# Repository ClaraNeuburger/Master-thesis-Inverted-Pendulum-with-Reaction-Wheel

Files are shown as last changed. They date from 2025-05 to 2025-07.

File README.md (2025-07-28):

# Inverted Pendulum Actuated by a Reaction Wheel

This github repository contains the codes (Arduino and Matlab) and CAD files used to create a 2D inverted pendulum actuated by a reaction wheel. 
This project was carried out to support the teaching of control engineering at the SAAS (Service d’Automatique et d’Analyse des Systèmes, https://saas.ulb.ac.be/) laboratory at ULB. The resulting Master thesis text is also available in this repository under *'Master Thesis Text.pdf'*.

## Overview
It consists of a rigid pendulum rod placed on a surface which will be stabilized in the upright position using a motor coupled to a wheel placed on top of the pendulum as shown bellow. 

<p align="center">
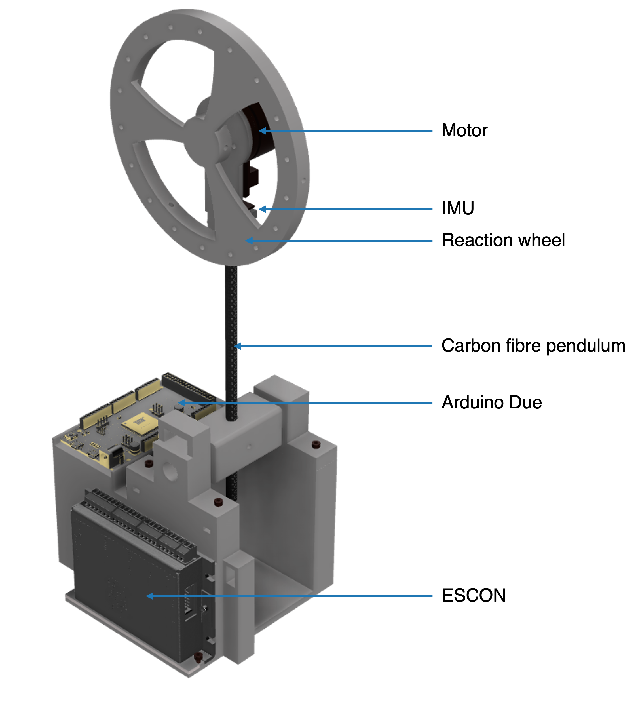
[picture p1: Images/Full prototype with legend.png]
  
</p>

A video of the working prototype is available in the following link: https://www.youtube.com/shorts/VWwU4DCKMfk

The following sections provide a detailed description of the prototype development process. They cover the design and fabrication of 3D-printed components, the selection of the motor and its integration with the driver and the choice and programming of the microcontroller.

## Microcontroller
The Arduino Due was selected as the development board for this project due to its higher computational performance and advanced features. Its 84 MHz clock speed enables faster signal processing, essential for real-time applications. The Due provides a DAC (Digital-to-Analog Converter) for smoother analog outputs, as well as a larger SRAM (96 kB), allowing efficient handling of complex computations and storage of runtime variables.

<p align="center">
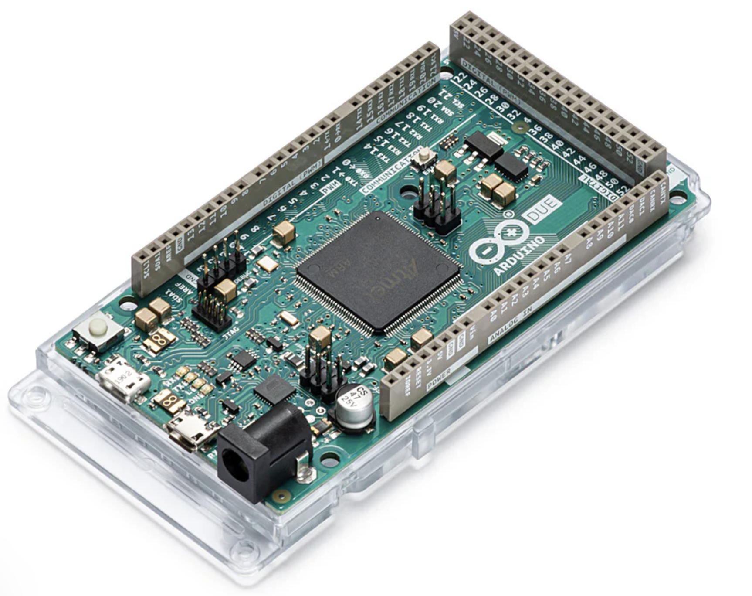
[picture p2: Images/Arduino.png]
  
</p>

The codes implemented on the microcontroller for controlling the pendulum are available in the folder 'Arduino'. 

- Scripts starting with *MPU6050* handle the data received from the Inertial Measurement Unit (IMU) and taken from: https://github.com/jrowberg/i2cdevlib
- File *Variables.ino* defines all variables used for the real time control of the pendulum
- File *main.ino* conatins the live script for controlling the pendulum

## Motor
The motor should be as lightweight as possible while also providing maximum torque. A Maxon brushless DC motor was selected: the EC 45 Flat. 
<p align="center">
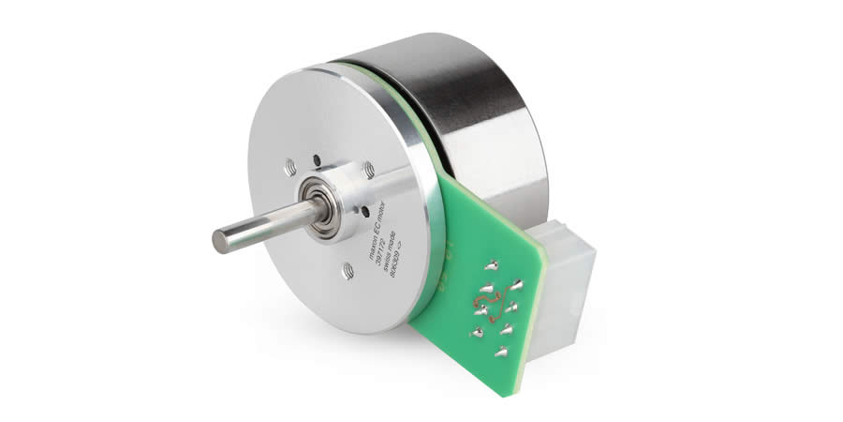
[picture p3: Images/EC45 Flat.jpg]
  
</p>

This type of motor offers an attractive price to performance ratio, a high torques due to external multipole rotor, and a flat and light design meant for limited space. 
The properties of the motor are shown in the table bellow.
<p align="center">
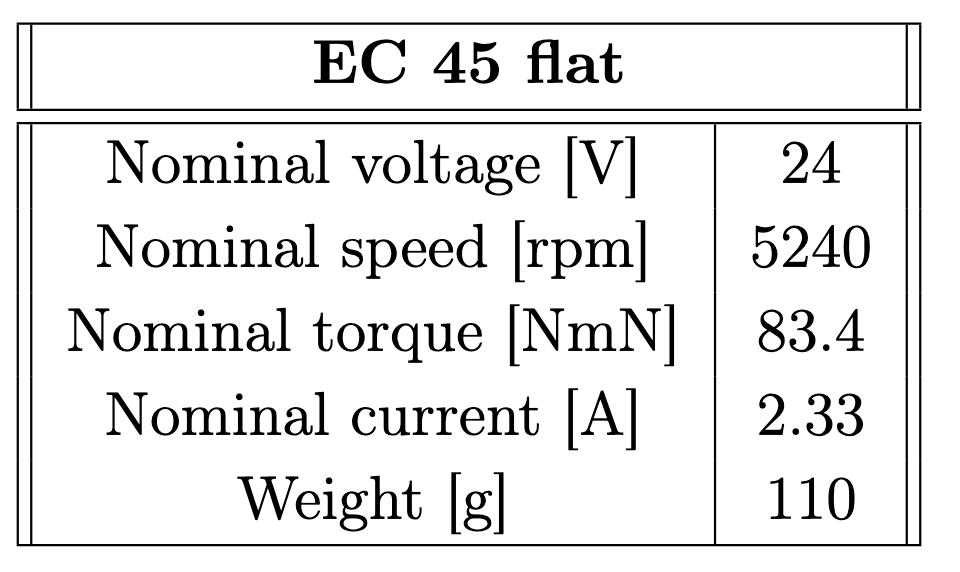
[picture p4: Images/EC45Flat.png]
  
</p>

Link for the motor: https://befr.rs-online.com/web/p/dc-motors/0495063
## Driver
In order to control the motor using the microcontroller, a driver needs to be used. A driver serves as the interface between the motor and the microcontroller to control the motor’s speed, direction or other parameter.

The ESCON 50/5 from Maxon compatible with the motor was chosen. 
<p align="center">
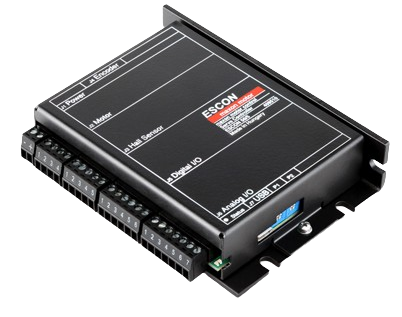
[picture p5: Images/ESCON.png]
  
</p>

It has 3 integrated operating modes: 

 - Current controller which compares the actual motor current with the applied set value and dynamically adjusts it in case of deviation
 - Closed loop speed controller that compares the actual speed with the applied set value and dynamically adjusts it
 - Open loop speed controller that feeds the motor with a voltage proportional to theset value; the load changes are compensated with IxR methodology

The properties of the driver are shown in the table bellow. 
<p align="center">
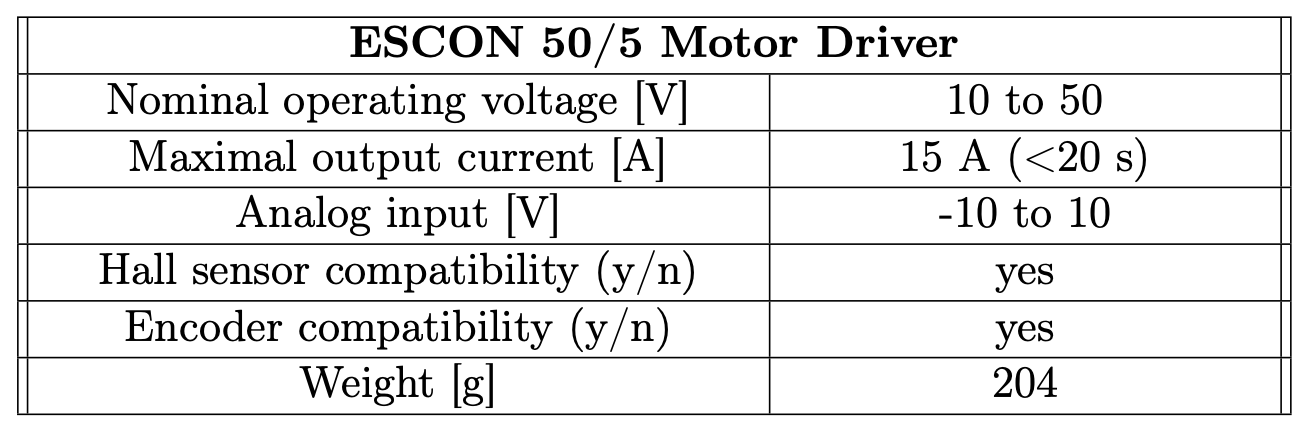
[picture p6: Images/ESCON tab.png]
  
</p>

The ESCON 50/5 is a programmable driver: on a software developed by Maxon, the user can enter the motor's propreties and select one of the 3 operating modes to control the motor. 

The following process was followed when laucnhing the start up wizard tool: 
- **Motor type**: Select maxon EC motor
- **Motor data**: Enter motor speed constant (285 rpm/V), thermal time constant winding (17.7s) and number of pole pairs (8)
- **System data**: Enter desired maximum speed (5240 rpm but you can increase if needed), nominal current (2.33 A) and max output current limit
- **Detection of rotor position**: Select digital Hall sensors with Maxon Hall sensor polarity
- **Speed sensor**: Select available Hall effect sensor
- **Mode of operation**: Select current controller
- **Enable**: Select your desired digital input with high active. In this situation, a switch was placed between digital Input 2 and the +5Vdc of the ESCON to easily enable the motor
- **Set value**: Select analog set value, with the analog input connected to the DAC pin of the microcontroller (here analog input 1). Since the Arduino DAC output is able to send voltages from 0.55 V to 2.75 V, the current sent at 0.55 V is set at -2.33 A and the current sent at 2.75 V is set at 2.33 A.
- ADD SPEED RAMP, OFFSET AND MINIMAL SPEED (need to check the computer for that)
- Add Analog output as well for understanding hall effect sensor outpur

A voltage of at least 22.79 V is required to power the ESCON 50/5 driving the EC45 Flat and a power supply of 24V has been selected. 

Link for the driver: https://www.maxongroup.fr/maxon/view/product/control/4-Q-Servokontroller/409510
## Sensors
### Inertial Measurement Unit (IMU)
To recover the pendulum angle and angular speed an inertial measurement unit can be used. It consists of a combination of accelerometer and gyroscope that allows to measure and report the angular rate of a structure. The accelerometer measures changes of acceleration in the sensor with respect to the earth while the gyroscope measures changing angular motion. The chosen IMU is the MPU6050 linked to an I2C bus for easier connection with the Arduino microcontroller 

<p align="center">
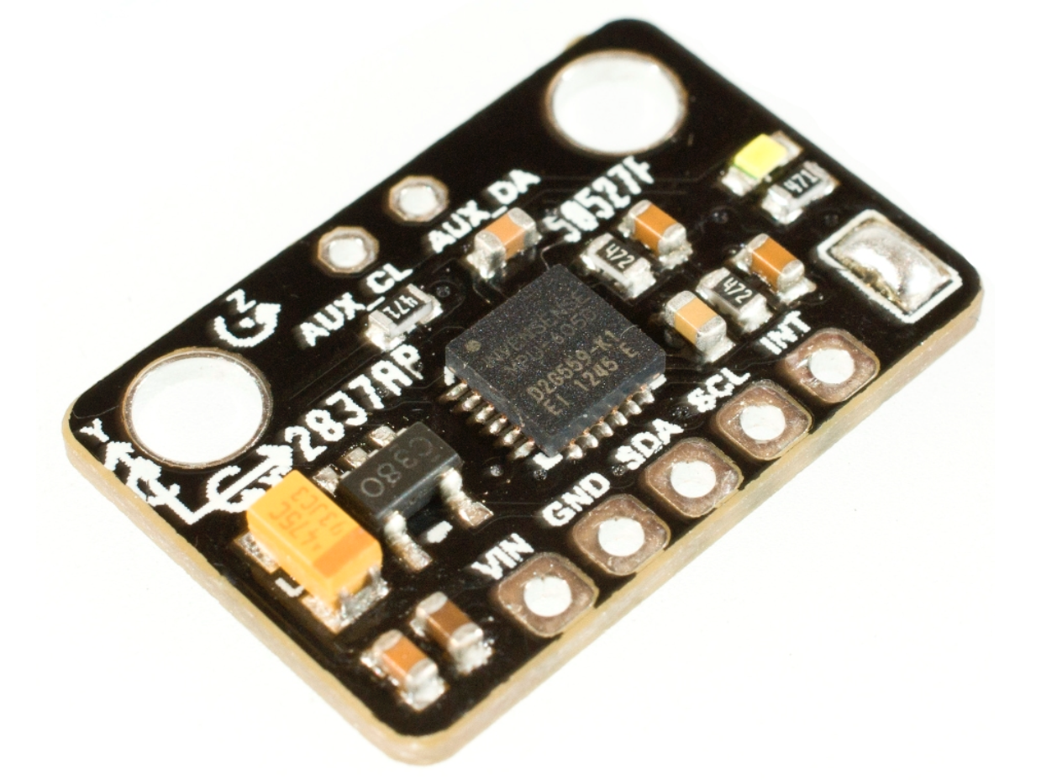
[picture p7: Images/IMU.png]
  
</p>

It has a 3 axis gyroscope and accelerometer, allowing to recover the angle and acceleration in the 3 planes(x,y,z). Using the MPU6050 Arduino library from i2cdevlib, it is
possible to retrieve the Euler angles of the pendulum with the function **mpu.dmpGetEuler()**. By filtering the angle value and doing a derivative, the pendulum angular velocity can also be determined.

Link for the MPU6050: https://be.farnell.com/fr-BE/dfrobot/sen0142/6-dof-sensor-arduino-board/dp/3769961
### Hall effect sensors
To measure the motor’s properties, the EC 45 Flat comes with integrated Hall sensors. Hall sensors detect the magnetic field of a control magnet which is attached to the shaft.
The sensors are arranged between the stator teeth and monitor directly the poles of the magnetic ring with offsets of 120°. The Hall sensors evaluate the direction of the magnetic field and generate a high output (5V) if the north pole of the control magnet is close and a low output (GND) if the south pole is close.

The ESCON 50/5 can automatically recover the motor’s speed and send it via a programmable analog output. The Arduino Due board can recover an analog input range of 0 to 3.3V and the ESCON drier is programmed to send a voltage of 0 V for a speed of -5240 rpm and 3.3 V for a speed ot 5240 rpm.

## Wiring diagram
The wiring diagram of the inverted pendulum with reaction wheel is illustrated bellow.
<p align="center">
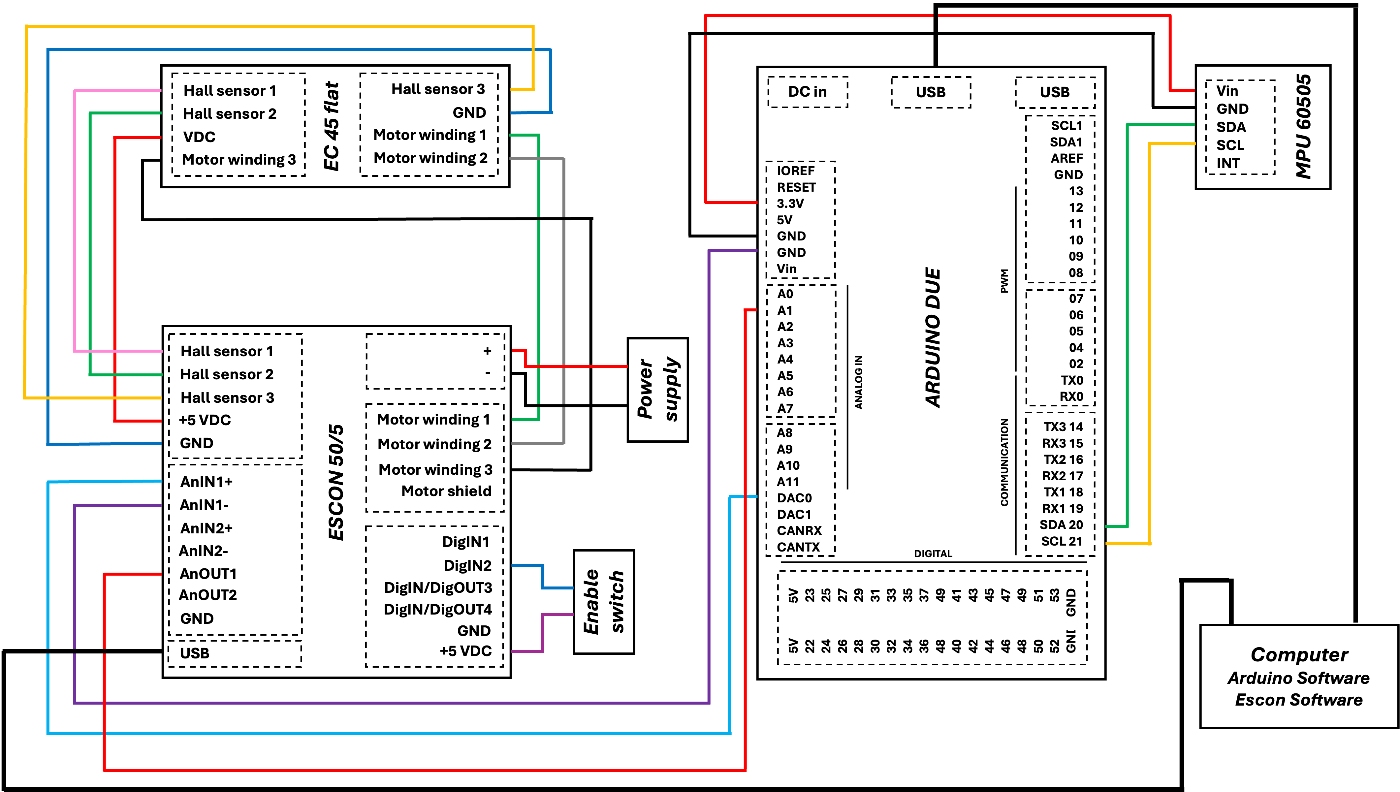
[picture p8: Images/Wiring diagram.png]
  
</p>

## 3D design and printing
The prototype was mainly 3D-printed except for the pendulum rod made of carbon fiber (30cm long hollow cylinder of outer radius 7.5mm). All other components were designed on Fusion360 and 3D-printed in PLA. The CAD files are available in the folder *'Fusion360'*.

A short readme is available in this folder and explains the role of each component and how they are connected to each other. 

The final prototype is shown bellow.
<p align="center">
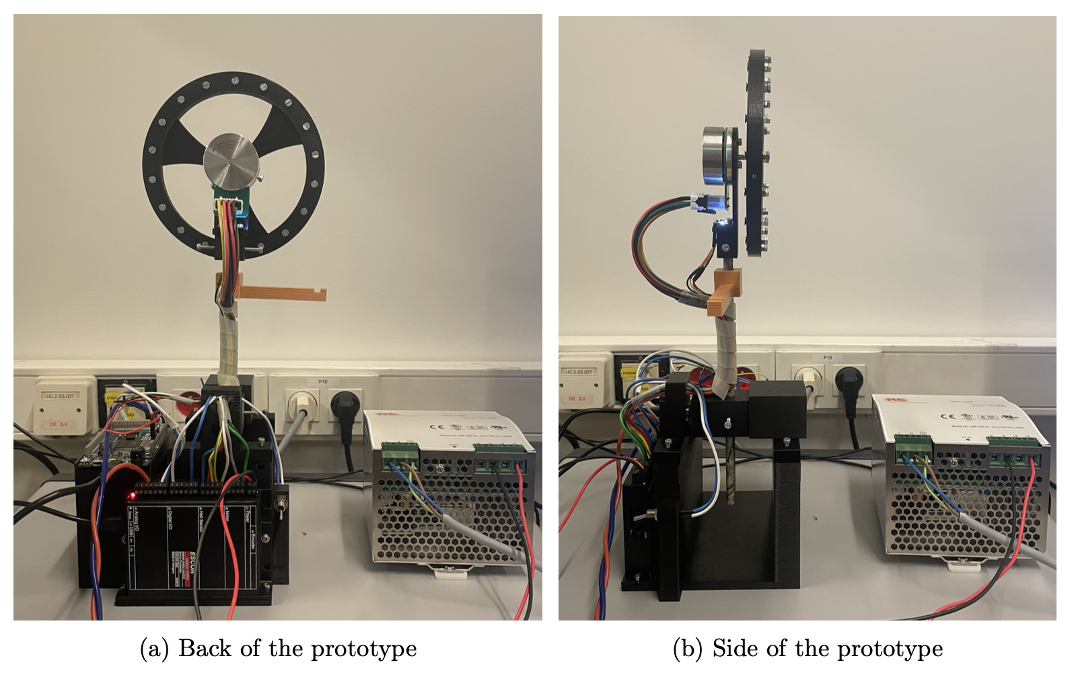
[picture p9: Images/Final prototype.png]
  
</p>

## Matlab code for controlling the pendulum
A series of Matlab code and simulations is available in the folder *Matlab* of this Github. They were developed to establish the control laws to control the pendulum. 

Firstly, a mathematical model of the pendulum was developed and verified experimentally. This is developed in the section *'Mathematical model'* of the Master thesis text.  The code *'model_verif.m'* is used to superpose the experimental results to the simulation results computed by using Simulink file *'Verification_simulink.slx'*. The pendululm was placed upside down, with a current command of 1A during 1 second.

Codes *'Identification_TF.m'*, *'cost_TF.m'* and *'verification.m'* are used to identify and verify the transfer function of the motor (speed response to a current step input).

There are 2 controllers tested: a cascade PID controller and an Linear Quadratic Regulator. The LQR is tuned and the gain is computed using the code *'LQR.m'*, it can then be verified using the simulation *'RegulatorTesting.slx'*.

The cascade PID is tuned using code *'CascadePID.m'* and tested using simulation *'PIDcascadeTuning.slx'*.

Only the LQR worked experimentally, more details are available in the written master thesis.

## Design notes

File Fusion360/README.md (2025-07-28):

This folder contains all the pieces designed on Fusion3D software and 3D printed to create the inverted pendulum with reaction wheel prototype. 

The support structure serves as base to receive the microcontroller (Arduino) and driver (ESCON). They however have some dimensioning issue in terms of the holes to insert screws to secure the 2 parts. 
<p align="center">
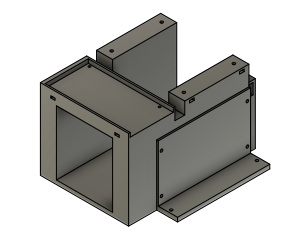
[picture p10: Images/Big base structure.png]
  
</p>

On this support structure are placed 2 'base structure' shown bellow. One is designed with a hole on top to allow the cables to directly reach the top of the driver for connection. 
<p align="center">
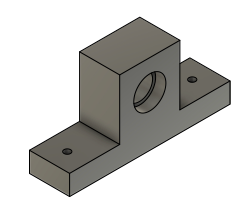
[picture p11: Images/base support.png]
  
</p>

<p align="center">
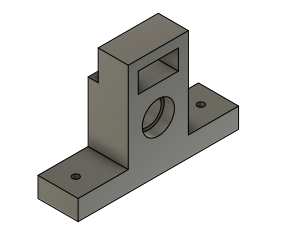
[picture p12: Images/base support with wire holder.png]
  
</p>

Between those 2 bases are places ball bearings (add dimensions) as well as a rectangular holder in which the pendulum is placed and secured with screws. 
<p align="center">
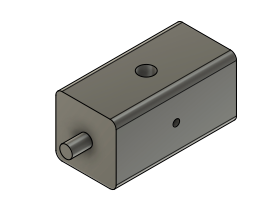
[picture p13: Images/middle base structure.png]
  
</p>

On top of the pendulum is placed the upper structure meant to link with the motor and the inertial measurement unit.
<p align="center">
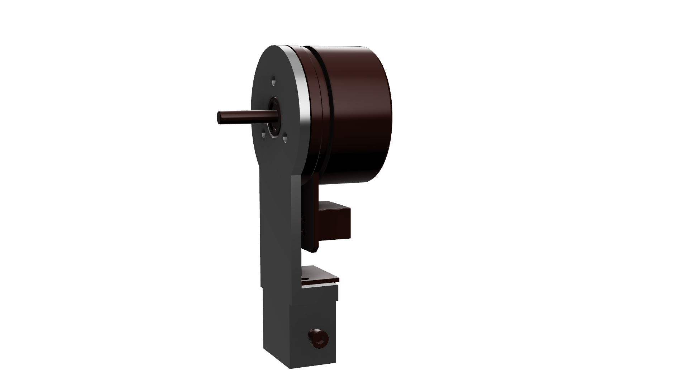
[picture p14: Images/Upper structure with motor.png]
  
</p>

 The reaction wheel is linked to the motor and holes are designed to add screws and nuts to increase its inertia. 
 
<p align="center">
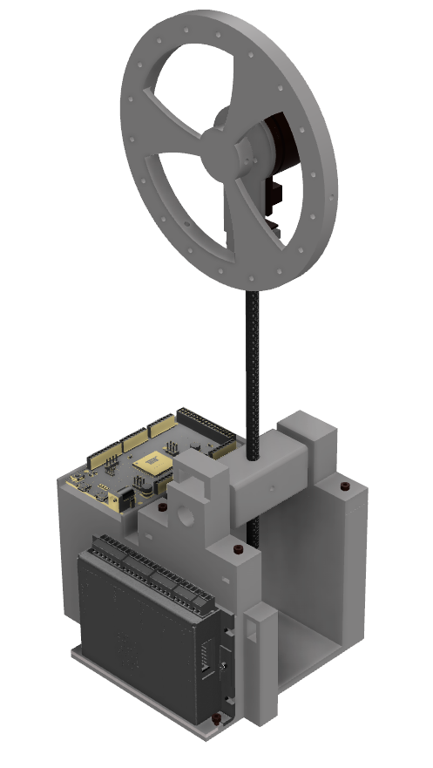
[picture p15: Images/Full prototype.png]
  
</p>

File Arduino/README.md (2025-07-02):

This folder contains all the Arduino scripts used to control the pendulum. 

All the files meant to recover the pendulum's variables from the inertial measurement unit start with 'MPU6050' and where taken from: https://github.com/jrowberg/i2cdevlib

File MPU6050.ino is meant to recover the pendulum angle during live script. 

File Variables.ino defines all variables used in the main file. 

The main.ino file contains the live script to control the Arduino. It recovers the pendulum angle, angular speed and reaction wheel speed to compute the control law using a Linear Quadratic Regulator. It then sends the corresponding DAC value to the microcontroller to control the motor. The current control loop of the ESCON must be previously tuned to achieve control in command.

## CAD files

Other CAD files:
Fusion360/Base structure with cable holder.f3d
Fusion360/Base structure.f3d
Fusion360/Piece for weight holding.f3d
Fusion360/Reaction wheel.f3d
Fusion360/Rectangular holder.f3d
Fusion360/Support structure.f3d
Fusion360/Upper structure.f3d

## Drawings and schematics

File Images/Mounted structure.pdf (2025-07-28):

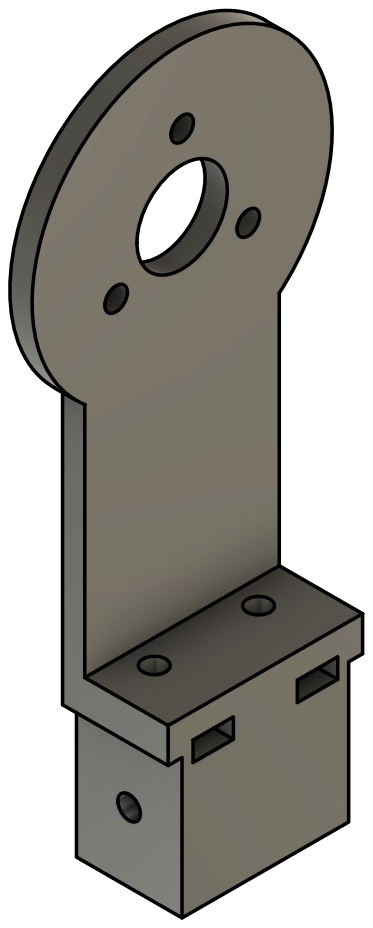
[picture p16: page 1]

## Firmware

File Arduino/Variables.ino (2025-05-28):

#include "I2Cdev.h"
#include "MPU6050_6Axis_MotionApps20.h"
#include "Wire.h"


////////////////////////////////////////////
// PIN Assignments //
////////////////////////////////////////////

#define DAC_PIN DAC0
#define A1_PIN A1

#define pin_IMU_interrupt 2
#define pin_IMU_SDA 20
#define pin_IMU_SCL 21


////////////////////////////////////////////
// Variables for sampling //
////////////////////////////////////////////
float current_time;
float previous_time;
float time0;

const float t_cycle = 100; // 1ms
const int t_exp = 10000000; //(10sec)
const int nb_cycles = t_exp/t_cycle;
const int t_start = 1000000; 
const int t_end = 11000000;



////////////////////////////////////////////
// Variables for Theta Calculations //
////////////////////////////////////////////

float theta_time = 0; // Time of Theta calculation
float cycle_time = 0; // Time since last Theta calculation

float theta= 0; // Pendulum angle
float theta_prev = 0; //Previous pendulum angle
float dTheta = 0; // Pendulum Angular velocity  
float dTheta_prev = 0; // Previous angular velocity of pendulum

////////////////////////////////////////////
// Controller Variables //
////////////////////////////////////////////
float dac_value = 0;
float command = 0;
float command_prev = 0;

//float const K1 = 0.6583;
//float const K2 = 0.2785;
//float const K3 = 0.0003;

/*
// With older coefficient between position and speed
float const K1= 0.9812;
float const K2= 0.1142;
float const K3= 0.0011;
*/

// new coeff: works very well also!
float const K1= 0.8912;
float const K2= 0.1142;
float const K3= 0.0011;

/*
//New model R = 1e7
float const K1 = 0.6804;
float const K2 = 0.0931;
float const K3 = 0.0031;
*/
/*
//New model R = 1e7 T = 6
float const K1 = 0.5736;
float const K2 = 0.0789;
float const K3 = 0.0031;
*/

/*
//New model R = 1e7 T = 6 I = 0.011, bp = 0.03
float const K1 = 0.6538;
float const K2 = 0.0763;
float const K3 = 0.0031;
*/

const int NB_DATA=5000;
float tab_error_out[NB_DATA];
float tab_speedref_motor[NB_DATA];
float ref_speed=0;

/*
float const a = -178.9;
float const b = 352.4;
float const c = -173.6;
float const d = -1.991;
float const e = 0.991;
*/

float const a = -1040;
float const b = 17810;
float const c = -7621;
float const d = -0.1994;
float const e = -0.02968;



////////////////////////////////////////////
// Motor Speed Variables //
////////////////////////////////////////////

float current_speed = 0;
float filtered_speed = 0;
float previous_speed = 0;
float smoothing = 0.99;

////////////////////////////////////////////
// SETUP PROCEDURE //
//////////////////////////////////////////// 

void setup() {
Serial.begin(115200);

pinMode(DAC_PIN,OUTPUT);
pinMode(A1_PIN,INPUT);

pinMode(pin_IMU_interrupt, INPUT);

IMU_setup();
dac_value = 0*(4095/4.66)+2047.5;
dac_value = constrain(dac_value,0,4095);
analogWrite(DAC_PIN,dac_value);
}

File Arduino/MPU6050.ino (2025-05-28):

// I2C device class (I2Cdev) demonstration Arduino sketch for MPU6050 class using DMP (MotionApps v2.0)
// 6/21/2012 by Jeff Rowberg <jeff@rowberg.net>
// Updates should (hopefully) always be available at https://github.com/jrowberg/i2cdevlib
//
// Changelog:
// 2019-07-08 - Added Auto Calibration and offset generator
// - and altered FIFO retrieval sequence to avoid using blocking code
// 2016-04-18 - Eliminated a potential infinite loop
// 2013-05-08 - added seamless Fastwire support
// - added note about gyro calibration
// 2012-06-21 - added note about Arduino 1.0.1 + Leonardo compatibility error
// 2012-06-20 - improved FIFO overflow handling and simplified read process
// 2012-06-19 - completely rearranged DMP initialization code and simplification
// 2012-06-13 - pull gyro and accel data from FIFO packet instead of reading directly
// 2012-06-09 - fix broken FIFO read sequence and change interrupt detection to RISING
// 2012-06-05 - add gravity-compensated initial reference frame acceleration output
// - add 3D math helper file to DMP6 example sketch
// - add Euler output and Yaw/Pitch/Roll output formats
// 2012-06-04 - remove accel offset clearing for better results (thanks Sungon Lee)
// 2012-06-01 - fixed gyro sensitivity to be 2000 deg/sec instead of 250
// 2012-05-30 - basic DMP initialization working

/* ============================================
I2Cdev device library code is placed under the MIT license
Copyright (c) 2012 Jeff Rowberg

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
THE SOFTWARE IS PROVIDED "AS IS", WITHOUT WARRANTY OF ANY KIND, EXPRESS OR
IMPLIED, INCLUDING BUT NOT LIMITED TO THE WARRANTIES OF MERCHANTABILITY,
FITNESS FOR A PARTICULAR PURPOSE AND NONINFRINGEMENT. IN NO EVENT SHALL THE
AUTHORS OR COPYRIGHT HOLDERS BE LIABLE FOR ANY CLAIM, DAMAGES OR OTHER
LIABILITY, WHETHER IN AN ACTION OF CONTRACT, TORT OR OTHERWISE, ARISING FROM,
OUT OF OR IN CONNECTION WITH THE SOFTWARE OR THE USE OR OTHER DEALINGS IN
THE SOFTWARE.
===============================================
*/

// I2Cdev and MPU6050 must be installed as libraries, or else the .cpp/.h files
// for both classes must be in the include path of your project
#include "I2Cdev.h"

#include "MPU6050_6Axis_MotionApps20.h"
//#include "MPU6050.h" // not necessary if using MotionApps include file

// Arduino Wire library is required if I2Cdev I2CDEV_ARDUINO_WIRE implementation
// is used in I2Cdev.h
#if I2CDEV_IMPLEMENTATION == I2CDEV_ARDUINO_WIRE
#include "Wire.h"
#endif

// class default I2C address is 0x68
// specific I2C addresses may be passed as a parameter here
// AD0 low = 0x68 (default for SparkFun breakout and InvenSense evaluation board)
// AD0 high = 0x69
MPU6050 mpu;
//MPU6050 mpu(0x69); // <-- use for AD0 high

/* =========================================================================
NOTE: In addition to connection 3.3v, GND, SDA, and SCL, this sketch
depends on the MPU-6050's INT pin being connected to the Arduino's
external interrupt #0 pin. On the Arduino Uno and Mega 2560, this is
digital I/O pin 2.
* ========================================================================= */

/* =========================================================================
NOTE: Arduino v1.0.1 with the Leonardo board generates a compile error
when using Serial.write(buf, len). The Teapot output uses this method.
The solution requires a modification to the Arduino USBAPI.h file, which
is fortunately simple, but annoying. This will be fixed in the next IDE
release. For more info, see these links:

http://arduino.cc/forum/index.php/topic,109987.0.html
http://code.google.com/p/arduino/issues/detail?id=958
* ========================================================================= */



#define OUTPUT_READABLE_EULER


// MOTOR
#define DAC_PIN DAC0
#define A1_PIN A1

#define INTERRUPT_PIN 2 // use pin 2 on Arduino Uno & most boards
#define LED_PIN 13 // (Arduino is 13, Teensy is 11, Teensy++ is 6)




bool blinkState = false;

// MPU control/status vars
bool dmpReady = false; // set true if DMP init was successful
uint8_t mpuIntStatus; // holds actual interrupt status byte from MPU
uint8_t devStatus; // return status after each device operation (0 = success, !0 = error)
uint16_t packetSize; // expected DMP packet size (default is 42 bytes)
uint16_t fifoCount; // count of all bytes currently in FIFO
uint8_t fifoBuffer[64]; // FIFO storage buffer

// orientation/motion vars
Quaternion q; // [w, x, y, z] quaternion container
VectorInt16 aa; // [x, y, z] accel sensor measurements
VectorInt16 aaReal; // [x, y, z] gravity-free accel sensor measurements
VectorInt16 aaWorld; // [x, y, z] world-frame accel sensor measurements
VectorFloat gravity; // [x, y, z] gravity vector
float euler[3]; // [psi, theta, phi] Euler angle container
float ypr[3]; // [yaw, pitch, roll] yaw/pitch/roll container and gravity vector
float angle;
// packet structure for InvenSense teapot demo
uint8_t teapotPacket[14] = { '$', 0x02, 0,0, 0,0, 0,0, 0,0, 0x00, 0x00, '\r', '\n' };



//ref_speed = -e*tab_speedref_motor[j-2] -d*tab_speedref_motor[j-1] ;
//         + a*tab_error_out[j] + b*tab_error_out[j-1] + c*tab_error_out[j-2];

// ================================================================
// === INTERRUPT DETECTION ROUTINE ===
// ================================================================

volatile bool mpuInterrupt = false; // indicates whether MPU interrupt pin has gone high
void dmpDataReady() {
mpuInterrupt = true;
}


// ================================================================
// === INITIAL SETUP ===
// ================================================================

void IMU_setup() {
// join I2C bus (I2Cdev library doesn't do this automatically)
#if I2CDEV_IMPLEMENTATION == I2CDEV_ARDUINO_WIRE
Wire.begin();
Wire.setClock(400000); // 400kHz I2C clock. Comment this line if having compilation difficulties

#elif I2CDEV_IMPLEMENTATION == I2CDEV_BUILTIN_FASTWIRE
Fastwire::setup(400, true);
#endif

pinMode(DAC_PIN,OUTPUT);
pinMode(A1_PIN,INPUT);
analogWriteResolution(12);
analogReadResolution(12);

  // ================================================================
  // Initialize motor
  // ================================================================

//delay(200);
// initialize serial communication
// (115200 chosen because it is required for Teapot Demo output, but it's
// really up to you depending on your project)
//Serial.begin(115200);
Serial.begin(115200);


while (!Serial);
// NOTE: 8MHz or slower host processors, like the Teensy @ 3.3V or Arduino
// Pro Mini running at 3.3V, cannot handle this baud rate reliably due to
// the baud timing being too misaligned with processor ticks. You must use
// 38400 or slower in these cases, or use some kind of external separate
// crystal solution for the UART timer.

// initialize device
Serial.println(F("Initializing I2C devices..."));
mpu.initialize();
pinMode(INTERRUPT_PIN, INPUT);

// verify connection
Serial.println(F("Testing device connections..."));
Serial.println(mpu.testConnection() ? F("MPU6050 connection successful") : F("MPU6050 connection failed"));

// wait for ready
Serial.println(F("\nSend any character to begin DMP programming and demo: "));
while (Serial.available() && Serial.read()); // empty buffer
while (!Serial.available()); // wait for data
while (Serial.available() && Serial.read()); // empty buffer again

// load and configure the DMP
Serial.println(F("Initializing DMP..."));
devStatus = mpu.dmpInitialize();

// supply your own gyro offsets here, scaled for min sensitivity
//mpu.setXGyroOffset(220);
//mpu.setYGyroOffset(76);
//mpu.setZGyroOffset(-85);
//mpu.setZAccelOffset(1788); // 1688 factory default for my test chip
mpu.setXGyroOffset(0);
mpu.setYGyroOffset(0);
mpu.setZGyroOffset(0);
mpu.setZAccelOffset(0);
// make sure it worked (returns 0 if so)
if (devStatus == 0) {
// Calibration Time: generate offsets and calibrate our MPU6050
mpu.CalibrateAccel(6);
mpu.CalibrateGyro(6);
mpu.PrintActiveOffsets();
// turn on the DMP, now that it's ready
Serial.println(F("Enabling DMP..."));
mpu.setDMPEnabled(true);

// enable Arduino interrupt detection
Serial.print(F("Enabling interrupt detection (Arduino external interrupt "));
Serial.print(digitalPinToInterrupt(INTERRUPT_PIN));
Serial.println(F(")..."));
attachInterrupt(digitalPinToInterrupt(INTERRUPT_PIN), dmpDataReady, RISING);
mpuIntStatus = mpu.getIntStatus();

// set our DMP Ready flag so the main loop() function knows it's okay to use it
Serial.println(F("DMP ready! Waiting for first interrupt..."));
dmpReady = true;

// get expected DMP packet size for later comparison
packetSize = mpu.dmpGetFIFOPacketSize();
} else {
// ERROR!
// 1 = initial memory load failed
// 2 = DMP configuration updates failed
// (if it's going to break, usually the code will be 1)
Serial.print(F("DMP Initialization failed (code "));
Serial.print(devStatus);
Serial.println(F(")"));
}

// configure LED for output
pinMode(LED_PIN, OUTPUT);
}



// ================================================================
// === MAIN PROGRAM LOOP ===
// ================================================================

void getIMUValues() {



       if (mpu.dmpGetCurrentFIFOPacket(fifoBuffer)) {
        //mpu.dmpGetCurrentFIFOPacket(fifoBmuffer);
        mpu.dmpGetQuaternion(&q, fifoBuffer);
     
        }
        mpu.dmpGetEuler(euler, &q);
        angle = euler[1]* 180/M_PI;
       
       

     
}

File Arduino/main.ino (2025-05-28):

////////////////////////////////////////////
// Main Loop //
////////////////////////////////////////////
void loop() {
while(micros()<t_start){
  dac_value = 0*(4095/4.66)+2047.5;
  dac_value = constrain(dac_value,0,4095);
  analogWrite(DAC_PIN,dac_value);
  getTheta();
}
while(micros()>=t_start && micros()<t_end){
  time0=micros();
  previous_time = time0;

  for(int j=0; j<nb_cycles;j++){
    current_time = micros();

    // Read Motor Speed
    getMotorSpeeds();

    // Calculate Theta and dTheta
    getTheta();

    // Let controller calculate set values for motors
    getRegulationLQR();

    // Set desired motor values
    setMotorSpeeds();

    // Print to Serial output for plotting
    printSerial();
    previous_time=current_time;
    while(micros()-time0 <(j+1)*t_cycle) {}
    
  }

  while(micros()>=t_end){
    setMotorSpeedsNull();
  }
  
}

}


////////////////////////////////////////////
// Calculate Motor Speeds in rad/s //
////////////////////////////////////////////
void getMotorSpeeds() {
  int raw_bit_value = analogRead(A1_PIN);
  current_speed = raw_bit_value*2.55 - 5240;
}


////////////////////////////////////////////
// Theta Calculations //
////////////////////////////////////////////
void getTheta(){
getIMUValues();
// Calculations for theta and dTheta
cycle_time = (float)(micros() - theta_time);
theta_time = (float) micros();
theta_prev = theta;
dTheta_prev = dTheta;
// Filter theta value
theta = (float) (1-0.7)*angle + 0.7*theta_prev;
// Find dTheta and apply filter
dTheta = (float) (theta - theta_prev)/cycle_time * 1000000.;
dTheta = (float) (1-0.7)*dTheta + 0.7*dTheta_prev;


}


////////////////////////////////////////////
// Controller Calculations for LQR //
// current control of the ESCON !  //
////////////////////////////////////////////
void getRegulationLQR(){
  if(theta < 11 && theta>-11){
    command = -(K1*angle + K2*dTheta + K3*(current_speed));
  }
  else {
    command = 0;
  }

// Security 
  if(command>2.33){
    command = 2.33;
  }
  if(command<-2.33){
    command = -2.33;
  }

}

////////////////////////////////////////////
// Set Motor output to desired value //
////////////////////////////////////////////

void setMotorSpeeds(){
if(command != command_prev){

    dac_value = command*(4095/4.66)+2047.5;
    dac_value = constrain(dac_value,0,4095);
    analogWrite(DAC_PIN,dac_value);

}
command_prev = command;
}


////////////////////////////////////////////
// Set Motor output to 0 (turn off motor) //
////////////////////////////////////////////

void setMotorSpeedsNull(){
    dac_value = 0*(4095/4.66)+2047.5;
    dac_value = constrain(dac_value,0,4095);
    analogWrite(DAC_PIN,dac_value);

}
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

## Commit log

2025-05-28 Arduino files
    [biplane.obj]
2025-07-23 Rename Capture d’écran 2025-07-23 à 15.26.37.png to EC45Flat.png
